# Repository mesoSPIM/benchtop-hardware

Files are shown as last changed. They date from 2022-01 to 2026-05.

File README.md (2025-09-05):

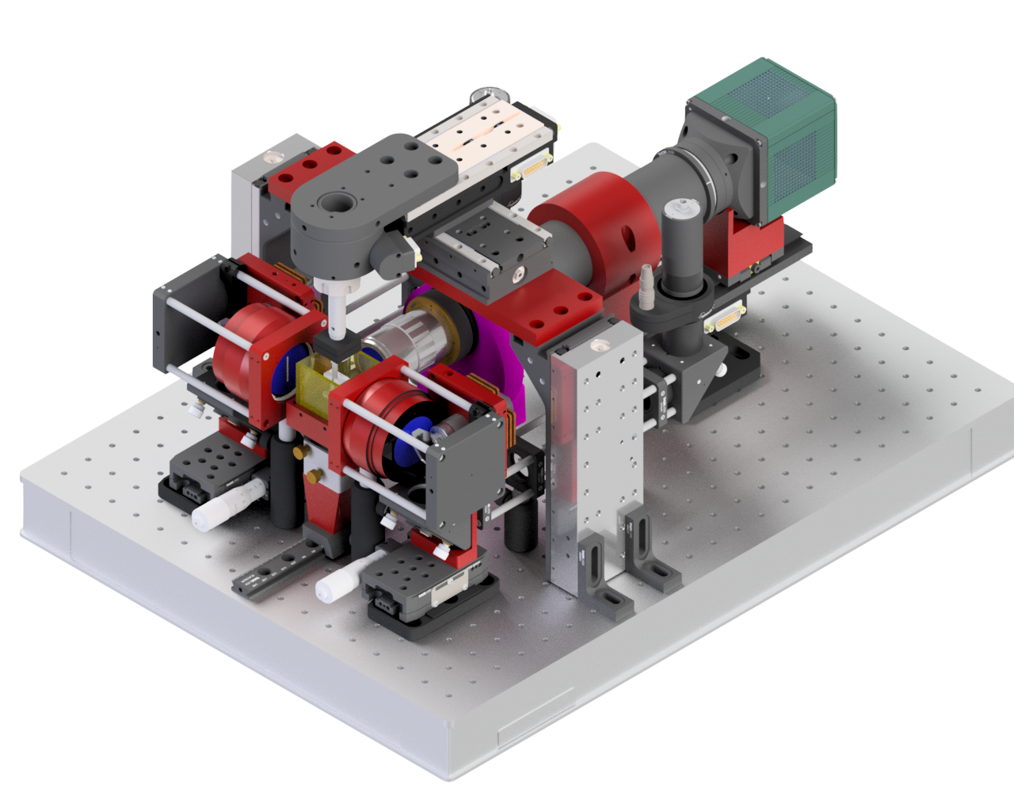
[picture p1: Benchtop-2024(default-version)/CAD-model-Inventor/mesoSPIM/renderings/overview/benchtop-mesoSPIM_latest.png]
Benchtop V2


# Benchtop mesoSPIM hardware documentation

## Who is the mesoSPIM project for?
* You are looking for a versatile imaging platform for cleared tissue that can be tailored to your needs.
* Research groups and imaging facilities with experience in building and supporting custom microscopes.

## What are ideal imaging applications for a mesoSPIM?
* screening of large numbers of cleared samples
* imaging of cell populations or other structures (blood vessels, plaques, denrites, even axons) in whole cleared organs.

## Why Benchtop mesoSPIM?
Being able to move the microscope from one lab to another, bring it to workshops, and send it to collaborators greatly increases its accessibility for biologists. Lab space is often a scarce asset, and having a compact microscope on the bench gives many advantages compared to bringing your samples to a large instrument in a dedicated room. 

## Key differences to mesoSPIM-v5
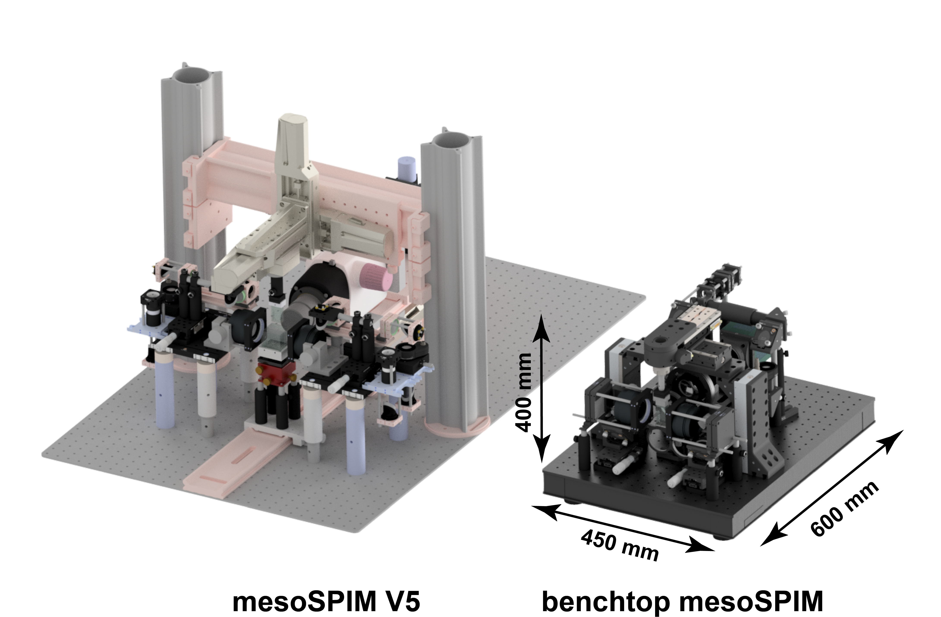
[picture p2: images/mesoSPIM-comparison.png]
mesoSPIM versions comparison


Benchtop mesoSPIM has smaller size, lower cost, higher image quality, and easier assembly than [previous version (V5)](https://github.com/mesoSPIM/mesoSPIM-hardware-documentation). 

| 					| **mesoSPIM v.5** | **Benchtop mesoSPIM** |
|----------|----------|--------------------|
|**Optical resolution, axial**| 5 $\mu m$ | 3.3 $\mu m$  | 
|**Optical resolution, lateral**| 2.7 $\mu m$ (at zoom 4x) | 2.0 $\mu m$ (1.5 - 2.6 $\mu m$ depending on the objective) | 
|**Magnification range**| 0.63x - 6.3x | 0.9x - 20x | 
| **Detection objectives** 	|  Variable magnification (via motorized zoom)  | Fixed-magnification (manual exchange) |
| **Camera sensor FOV (diagonal)** | 19 mm |  25 mm |
| **Pixel size** | 6.5 $\mu m$  | 4.25 $\mu m$  | 
| **Pixels/image** | 4 MP | 15 MP |
| **Footprint** | 1 $m^2$ |  0.25 $m^2$ |
| **Mobile** |  no | yes |
| **Approximate cost, EUR** | 162k | 95k | 

The cost estimate does not include PC workstation and a screen. V.5 costs include 4 laser lines (405, 488, 561, 638 nm) and optical table. Benchtop price includes the three most popular laser lines (488, 561, 638 nm) and 2x, 5x, 10x objectives. 

The number of custom parts in Benchtop is greatly reduced. 

The acquisition software remains the same, compatible with both versions of the microscope. 

## Build your own Benchtop
Our project is free and open-source, allowing anyone to build their own microscope. The [BT-mesoSPIM wiki](https://github.com/mesoSPIM/benchtop-hardware/wiki) will guide you how to build, setup, and use the BT-mesoSPIM system.

## Upgrade your existing v.4-5 mesoSPIM
(currently in beta) We also offer parts list and instructions for upgrading the detection optics of your existing mesoSPIM (v.4 and 5), so it can achieve the same resolution and image quality as the current Benchtop. See parts list and instructions for [mesoSPIM upgrade](https://github.com/mesoSPIM/benchtop-hardware/tree/main/v4-5-upgrade-2023).

# User guides
Introductory training of a new user typically takes 2 hours, ideally with a couple of follow-up sessions to make sure software parameters are set up correctly by the user. Our microscopy facility ZMB (Univerity of Zurich) has detailed guides on [mesoSPIM start-up, setting up, and acquisition](https://zmb.dozuki.com/c/Lightsheet_microscopy#Section_MesoSPIM).

## Citation
If you use any parts of this work for your project, please cite us:

Vladimirov, N., Voigt, F.F., Naert, T. et al. Benchtop mesoSPIM: a next-generation open-source light-sheet microscope for cleared samples. [Nat Commun 15, 2679 (2024).](https://doi.org/10.1038/s41467-024-46770-2)

## Discussion
Since August 2025 we joined the vibrant [image.cs forum](https://forum.image.sc/tag/mesospim)



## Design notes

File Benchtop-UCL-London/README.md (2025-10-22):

### UCL London version
This version of Benchtop mesoSPIM ([setup #29](https://mesospim.org/setups/)) was modified and shared by [Tchern Lenn](mailto:<y.lenn@ucl.ac.uk>) at the [UCL Cancer Institute Microscopy and Imaging Translational Technology Platform](https://www.ucl.ac.uk/cancer/research/cancer-institute-translational-technology-platforms/microscopy-and-imaging-translational). 

The advantages of this modification include:
- 6 laser lines
- alternative NI components for reduced cost

The key changes to the default setup:
- Filter wheel with 8 slots (ZWO EWF 8x31 mm).
- Elevation of the 3D printed detection path components to accomodate larger filter wheel
- NI signal generation card (PXIe-6738)
- NI Terminal block
- NI Card Chassis (PXIe-1090)
- Laser Combiner with 6 lasers

IMPORTANT NOTE!
The new chassis connects to the PC via a **thunderbolt** connection. No special card (eg. PCIe-8363) is needed but an available thunderbolt port on the PC is required.

## Files
Source files and parts list related to this version can be found above.

## Wiki
Wiki pages can be found [here](https://github.com/TchLenn/benchtop-hardware/wiki)

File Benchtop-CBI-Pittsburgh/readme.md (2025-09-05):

# Immersion chamber

- 3D printed using consumer-grade printer
- resistant to BABB, DBE, or other organic solvents
- low cost
- perfect alignment, no astigmatism
- robust against clumsy users
- thin walls, less spherical aberration
- large volume, fits large samples

# Documentation
[Mesospim cuvettes.pptx](./docs/Mesospim_cuvettes.pptx)


# Parts list
[Cuvette Parts List](./parts-list/parts-list-immersion-cuvette.xlsx)

## Credits
Designed at [CBI Pittsburgh](https://www.cbi.pitt.edu/) by Simon Watkins and Travis Wheeler.

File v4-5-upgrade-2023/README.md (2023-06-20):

*Currently in beta-testing!*

## Upgrade overview
Upgrading the detection objectives of your mesoSPIM can significantly boost your system resolution, while using newer cSMOS cameras (e.g. Teledyne Photometrics Iris 15 or Kinetix) can aditionally boost your throughput.

The suggested upgrade requires 5 Mitutoyo Plan Apo objectives (2x, 5x, 7.5x, 10x, 20x), a motorized turret, a compact filter wheel, mounting hardware, and, optionally, a large-sensor sCMOS camera (we recommend Teledyne Photometrics Iris 15).

SI-Fig-Detection-arm-upgrade

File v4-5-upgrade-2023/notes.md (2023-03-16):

## Ludl filter wheel
There are several problems with Ludl:
* they are bulky
* require custom adapters for Thorlabs SM2 lens tube
* over time the plastic belt can get torn
* require dedicated COM card and configuring COM port (which can change after Windows update)

## Zwo EFWmini filter wheel
Several advantages:
* small and low-cost (200$ vs 6k for Ludl)
* works from USB
* takes up filters up to 31 mm
* easy mechanical interface with T-mounts on each side, available from Thorlabs

### Detection arm optical axis height
From the upper rail carriage (Newport M-CXL95) to detection optical axis H=94 mm (v4,5)

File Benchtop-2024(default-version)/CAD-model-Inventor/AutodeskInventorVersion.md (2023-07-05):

# Autodesk Inventor version
The current version we are using is 2023. Unfortunately Autodesk keeps updating the version of our license, so there are some files that were created using 2017, 2019, or 2021 versions.

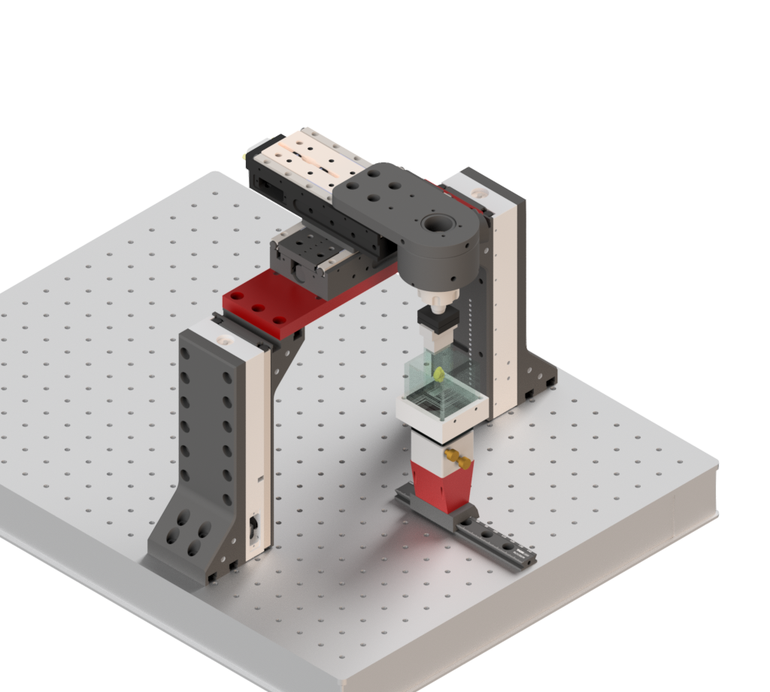
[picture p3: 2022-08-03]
Benchtop-2024(default-version)/CAD-model-Inventor/mesoSPIM/renderings/sample-stages-handling/stages-overview3.png

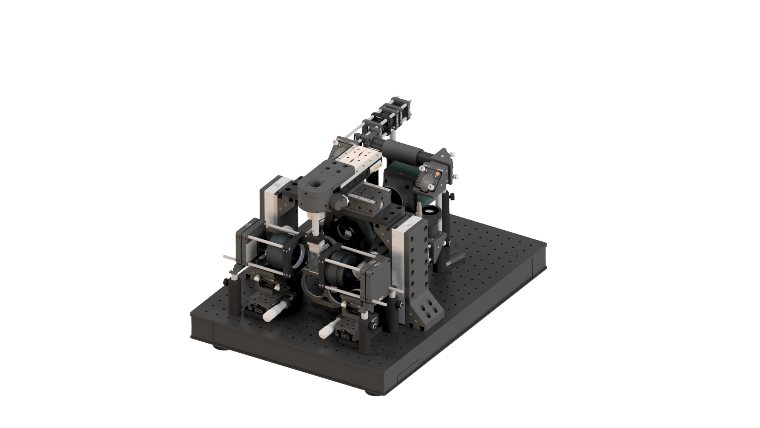
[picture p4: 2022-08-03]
Benchtop-2024(default-version)/CAD-model-Inventor/mesoSPIM/renderings/overview/view1/benchtop-mesoSPIM-V2-1-full.png

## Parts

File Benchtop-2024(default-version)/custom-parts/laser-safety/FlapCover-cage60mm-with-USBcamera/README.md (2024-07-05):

# Snap-on laser cover with integrated webcam mount for 60-mm Thorlabs cage system

# 3D printing
Extrusion printer (eg Prusa), PETG or similar material.

# Compatibe webcams
- `DFRobot FIT0701` (70-deg FOV)
- `HBVCAM-3M2111 V22` (110 deg FOV)

# Mounting hardware
- M3 screws 5 mm long screwed in directly into the holes.

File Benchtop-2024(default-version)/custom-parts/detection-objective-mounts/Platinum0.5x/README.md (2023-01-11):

## Warning
While it is possible to mount and use Edmund Platinum 0.5x telecentric lens with this mount, the galvo scanning range (for Thorlsbs 15-mm beam galvos) 
is too high to cover such large FOV at required frequency (100 Hz). As a result, the galvo flaps with weird noises.

So, use this lens at your own risk, possibly with smaller and lighter galvos, high-perfomance galvo driver, and watch for scanning issues.

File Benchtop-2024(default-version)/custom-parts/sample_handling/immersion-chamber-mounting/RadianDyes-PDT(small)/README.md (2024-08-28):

3D printed adapter for RadiantDyes RD-PDT-S (small) prism holder mounted on Thorlabs RC2 carier (dovetail rail).
- For cuvette height 45 mm, use `RD-PDT-S-to-RC2-height40mm.stl` model
- For cuvette height 75 mm, use `RD-PDT-S-to-M4-bolts-Base-H10mm.stl` model

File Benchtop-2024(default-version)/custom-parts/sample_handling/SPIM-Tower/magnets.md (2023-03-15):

Magnets size: D=2 mm, H=3-6 mm.

[Source in Switzerland](https://www.supermagnete.ch/stabmagnete-neodym-rund?length-or-diameter=2.00,2.00&height=3.00,3.00)

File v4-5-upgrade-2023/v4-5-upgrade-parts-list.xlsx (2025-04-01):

Part # | Vendor | Description | QTY | Unit Price (USD) | Price (USD) | Comment
Camera
01-IRIS-15-PCIe-M-16-C | Photometrics | IRIS-15-PCIe sCMOS camera | 1 | 12350.00 | 12350 | FOV 25 mm diagonal
Detection: Filter wheel
ZWO EFW 7x36mm | ZWO | ZWO EFW 7x36mm (https://astronomy-imaging-camera.com/product/new-zwo-efw-7x36mm/) | 1 | 299.00 | 299 | Check local distributors (astronomy shops). Alternative for small (25 mm) filters: 5-slot filter wheel for 25-mm filters
32mmFilterAdapter.stl | 3D printed (SLS) | Adapter to hold 32 mm filters in 36 mm slots | 5 | 10.00 | 50 | 32 mm filter in 36 mm slots (available 25mm filter for 31 mm slots). See /custom-parts/detection-accessories for printable 3D model
SM2T2 | Thorlabs | SM2 (2.035"-40) Coupler, External Threads, 1/2" Long | 1 | 37.00 | 37 | SM2 coupler to rotate the F mount (camera) relative to filter wheel
SM2V10 | Thorlabs | Ø2" Adjustable Lens Tube, 0.81" Travel | 1 | 54.00 | 54 | SM2 coupler to mount and rotate the turret relative to filter wheel
TMA4 | Thorlabs | Adapter with External T-Mount to Internal SM2 | 2 | 24.00 | 48 | Adapters for both sides of the ZWO EFW Mini filter, which has T-mount threads (M42)
Detection: objectives and revolver
5-slot motorized turret + 5 objectives
378-726D | Mitutoyo | Bright field motorized revolver | 1 | 4655.00 | 4655 | The turret for Mitutoyo Plan Apo objectives
12AAA807D | Mitutoyo | RS-232C cable 2 m | 1 | 75 | 75 | accessory
378-089 | Mitutoyo | Parfocal adjustment shim set | 1 | 136 | 136 | accessory
MotorizedRevolver-SM2-adapter | Mechanical shop | Adapter between motorized revolver and Thorlabs SM2 tube | 1 | 200 | 200 | Machined from Alu, requires SM2 threads
SM2L10 | Thorlabs | 1" long SM2 tube | 1 | 26.00 | 26 | Adapter: Motorized revolver to filter wheel. Replaced by SM2V10 to allow rotation.
378-801-12 | Mitutoyo | Objective M Plan APO 2X | 1 | 801 | 801
378-802-6 | Mitutoyo | Objective M Plan APO 5X | 1 | 718 | 718
378-807-3 | Mitutoyo | Objective M Plan APO 7.5X | 1 | 1391 | 1391
378-803-3 | Mitutoyo | Objective M Plan APO 10X | 1 | 883 | 883
378-847 | Mitutoyo | Mitutoyo G Plan APO 20X/t3,5 (https://shop.mitutoyo.ch/web/mitutoyo/en_CH/mitutoyo/05.04.02/G%20Plan%20APO%2020X-t3%2C5/PR/378-847/index.xhtml;jsessionid=CFD835C47751CA929FEA384183C0A21D) | 1 | 3670.00 | 3670
Detection: Tube lens and camera F-mount
36-401 | Edmund Optics | Mitutoyo MT-1 Accessory Tube Lens (https://www.edmundoptics.com/p/mt-1-accessory-tube-lens/11488/) | 1 | 752.00 | 752 | Preferred choice for Mititoyo objectives, except the 2X/0.055 one. Ordered from Edmund for historical reasons, update part number to Mitutoyo
Adapter-MitutoyoMT1-SM2-v3(flex).stl | 3D printed | Adapter for SM2 lens tube, attached to SM2 retaining ring | 1 | 50.00 | 50
SM2E60 | Thorlabs | SM2 Series Extension Tube, 6" | 1 | 65.00 | 65 | Tube lens is inserted inside this tube
SM2M20 | Thorlabs | SM2 Lens Tube Without External Threads, 2" Thread Depth | 1 | 32.00 | 32 | Extends the SM2E60 and mounts to the SM2NFM2
SM2NFM2 | Thorlabs | Adapter with External SM2 Threads and Male F-Mount Ring | 1 | 112.00 | 112 | Adapter to camera with F-mount
 |  |  |  | 584.00
Detection Assembly Mounting (on the X95 rail carriage)
ThorlabsSM2L30-XT66P2M_H94mm(axis2base) | 3D printed | Rail carriage mount of the SM2 tube assembly | 2 | 50 | 100 | Bolted to the Newport CXL95 rail carriages (M6 bolts)
XT95-500 | Thorlabs | 95 mm Construction Rail, Clear Anodized, L = 500 mm | 3 | 150 | 0 | Gantry elements, ONLY for mesoSPIM-v4 upgrade
XT95P3 | Thorlabs | Base Plate for 95 mm Rails | 2 | 53 | 0 | Gantry elements, ONLY for mesoSPIM-v4 upgrade
XT95RC4/M | Thorlabs | Drop-On Rail Carriage for 95 mm Rails, 100.0 mm Long, M6 Tapped Holes | 3 | 128 | 0 | Gantry elements, ONLY for mesoSPIM-v4 upgrade
XT95RC1/M | Thorlabs | Drop-On Rail Carriage for 95 mm Rails, 25.0 mm Long, M6 Tapped Holes | 2 | 77 | 0 | Gantry elements, ONLY for mesoSPIM-v4 upgrade
camera-dependent | camera-dependent | Camera-specific support structure | 1 | 50 | 50 | Photometrics Iris 15: ToDo. Orca Lightning: Breadboard 200 mm wide that supports the weight of the camera
 |  |  |  | Total, USD | 26554

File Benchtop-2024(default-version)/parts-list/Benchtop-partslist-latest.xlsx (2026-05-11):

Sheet: Main
DISCLAIMER: All prices are approximate and subject to change by the vendors without prior notice
Part # | Vendor | Description | QTY | Unit Price (USD) | Price (USD) | Assembly | Subassembly | Comment
Camera
01-IRIS-15-PCIe-M-16-C | Photometrics | IRIS-15-PCIe sCMOS camera | 1 | 15000 | 15000 | Detection arm |  | FOV 25 mm diagonal, programmable rolling shutter, 15MP sensor
Excitation laser combiner options
Recommended laser combiner specs: 3-4 lasers: (405 optional), 488, 561, 638 nm, power 50-150 mW. Digital and analog power modulation. Coupling to SM fiber with FC/APC end connector.
Currently recommended: | TOPTICA | CLE-50 combiner (405nm, 488nm, 561nm, 640nm: 50 mW each) | 2 | 29000 | 58000 | Excitation |  | Typically very stable and reliable lasers. For more budget lasers, CLE-20 or CLE-30 (20 and 30 mW per chanel) can be considered.
Legacy: | Oxxius | L4Cc 488-561-638 nm, 100 mW each, 2 fiber ports, switching module MDL-FSTM | 0 | 25000 | 0 | Excitation |  | Warning: Oxxius is a budget laser, with frequent quality issues. See overview at (https://github.com/mesoSPIM/benchtop-hardware/wiki/Laser-selection). Includes switching module between 2 laser ports, controlled by TTL signal. The 405nm is NOT included! A four-laser version is ~35k.
Sample & Microscope Stages
Dual-LS100-FTP-K0 | ASI | Two parallel LS-100 servo actuators, table mounting brackets not included | 0 | 6500 | 0 | Sample motion |  | Sample Y stage
LS-50-AMCCH | ASI | LS-50 Linear Stage, with sub-micron accuracy, and 50 mm of travel | 0 | 2250 | 0 | Sample motion |  | Sample X stage
LS-5012 | ASI | Plate for attaching flat surface of linear stage to breadboard. 3.9" x 5.9" | 0 | 160 | 0 | Detection arm | Detection path
LS-50-AMCLH | ASI | LS-50 Linear Stage, with sub-micron accuracy, and 50 mm of travel | 0 | 2250 | 0 | Detection arm | Detection path | Focus (F) stage, moves camera and detection lens assembly
DV-6010-C | ASI | Dovetail mount pair (VTS-2112 & CDZ-1010) 60 x 62 x 10 mm overall dimensions. | 0 | 230 | 0 | Sample motion |  | Cross-coupling X and Z stage adapter
LS-50S-AMECHS | ASI | LS-50 Linear Stage, with sub-micron accuracy, 50 mm of travel, and stainless steel slide | 0 | 2425 | 0 | Sample motion |  | Sample Z-stage
LE-LS-HH-70 | ASI | Encoder Linear LE Heidenhain 70mm scale installed on AMECHS stage | 0 | 3000 | 0 | Sample motion |  | Sample Z-stage encoder
C60-3060-CMR-1011 | ASI | LS-50 slide to C-mount adapter | 0 | 150 | 0 | Sample motion |  | Rotary stage adapter
C60-3060-SRS | ASI | Rotary stage with collet for holding a sample. | 0 | 3000 | 0 | Sample control |  | Sample Rotation (R) stage
STAGE-4D-MESOSPIM-K1 | ASI | All stage parts above offered by ASI (Jon Daniels <jon@asiimaging.com>) | 1 | 19965 | 19965 |  |  | Bundle of 6 stages with mounting hardware
TG8-BASIC | ASI | Controller: Includes TG8, TGCOM, 2x TGDCM2, SA-JOY+ZF Contols four DC servo motors, | 0 | 5800 | 0 | Motion control |  | Motion controller with pre-installed cards
TGDCM2-1RE | ASI | Dual Axis motion control card - one slot. Modified for 2nd axis always rotary encoded. | 0 | 1100 | 0 | Motion control |  | Motion controller card
TG8-MESOSPIM-K1 | ASI | The controller bundle offered by ASI | 1 | 6900 | 6900 |  |  | Bundle of motion controller
MESOS-11 or mesoSPIM-Bridge-wide | ASI or Mechanical shop | Bridge part between two parallel LS-100 servo actuators | 1 | 160 | 0 | Sample motion |  | Bridge for XZR stage assembly. NOT included in the STAGE-4D-MESOSPIM-K1 (above), but included in MESOS-MACH-K1 (below).
MESOS-MACH-K1 | ASI | kit of metal machined parts for benchtop mesoSPIM | 0 | 1740 | 1740 | Sample motion and Excitation |  | Kit includes MESOS-11, qty 14 MESOS-10, and qty 2 each MESOS-01, MESOS-12, and MESOS-13
AB90H | Thorlabs | Slim Right-Angle Bracket with Counterbored Slots | 5 | 27 | 135 | Sample motion |  | 4x: Table mounting for the Y axis (two parallel LS-100 servo actuators Dual-LS100-FTP); 1x: for galvo board heat sink mounting
Sample handling
KB25/M | Thorlabs | Complete 25 mm x 25 mm Kinematic Base, Top and Bottom Plates, M4 Counterbores | 2 | 70 | 140 | Sample handling |  | Magnetic bases to attach sample holders and immersion cuvette
KBB25/M | Thorlabs | Bottom Plate Only of the KB25/M Kinematic Base, M4 Counterbore | 6 | 36 | 216 | Sample handling |  | Sample holder side (nests, not balls) of the kinematic base
TR50/M | Thorlabs | Ø12.7 mm Optical Post, SS, M4 Setscrew, M6 Tap, L = 50 mm | 1 | 6 | 6 | Sample handling |  | Connection of theta-stage chuck to the sample holder.
PH50/M | Thorlabs | Ø12.7 mm Post Holder, Spring-Loaded Hex-Locking Thumbscrew, L=50 mm | 1 | 9 | 9 | Sample handling |  | Connection of theta-stage chuck to the sample holder. Use M6 bolt in the chuck to connect
RLA150/M | Thorlabs | Dovetail Optical Rail, 150 mm, Metric | 1 | 43 | 43 | Sample handling |  | Immersion cuvette base
RC2/M | Thorlabs | Dovetail Rail Carrier, 50.8 mm x 25.4 mm, M6 Counterbore, M4 Taps | 1 | 29 | 29 | Sample handling |  | Rail carrier for immersion cuvette base
RD-PDT-S | Radiant Dyes | Prism Turn Table Small | 1 | 195 | 195 | Sample handling |  | Base for immersion cuvette
RD-PDT-S-to-M4-bolts-Base-H10mm | 3D printed | Adapter for mounting RD-PDT-S to Thorlabs rail carrier RC2, cuvettes 75 mm tall | 1 | 10 | 10 |  |  | See file RD-PDT-S-to-M4-bolts-Base-H10mm.ipt (.stl) for details.
Computer
The following specs are suggested for acquisition, not for storage, visualization or image processing
CPU | Intel Xeon W-2145, W-2245 or Intel Core i9-9900K, or newer, high-performance for single-threaded applications
RAM | 128 GB DDR4
OS drive | 1 TB SSD NVMe
Fast storage (for streaming) | 2 TB or more SSD NVMe drive
IO | one PCIe x1 (or higher) and one PCIe x4 (or higher) slot.
OS | Windows 11 Pro LTSC
Monitor | 30 inch
Excitation arms
PBG52522 | Thorlabs | UltraLight Series II Breadboard, 450 x 600 x 55 mm, M6 Taps | 1 | 728 | 728 | Base |  | Microscope base
AV4/M | Thorlabs | Ø45.0 mm Sorbothane Feet, Internal M6 Mounting Thread, 4 Pieces | 1 | 33 | 33 | Base |  | Attached to the bottom of the PBG52522 Breadboard. Based on Benchtop weight 25 kg on breadboard (including BB).
SM1FCA | Thorlabs | FC/APC Fiber Adapter Plate with External SM1 (1.035"-40) Threads, Wide Key (2.2 mm) | 2 | 31 | 62 | Excitation | Laser collimator | Oxxius ships with PM-S405-XP+ optical fiber, NA=0.11.
AC254-060-A-ML | Thorlabs | f=60 mm, Ø1" Achromatic Doublet, SM1-Threaded Mount, ARC: 400-700 nm | 2 | 99 | 198 | Excitation | Laser collimator | Recommended achromat, depends of optical fiber NA, see https://github.com/mesoSPIM/benchtop-hardware/wiki/Excitation-arms-assembly
SM1M20 | Thorlabs | SM1 Lens Tube Without External Threads, 2" Long, Two Retaining Rings Included | 2 | 17 | 34 | Excitation | Laser collimator | This tube is minimal , for f=50 mm achromat. It must be extended by 0.3", 0.5" or 1" tubes for f=60, 70, or 75 mm achromats.
SM1L03 | Thorlabs | SM1 Lens Tube, 0.30" Thread Depth | 2 | 12 | 24 | Excitation | Laser collimator | Tube extension for f=60 mm achromat
SM1L05 | Thorlabs | SM1 Lens Tube, 0.50" Thread Depth | 2 | 12 | 24 | Excitation | Laser collimator | Tube extension for f=70 mm achromat
SM1L10 | Thorlabs | SM1 Lens Tube, 1" Thread Depth | 2 | 14 | 28 | Excitation | Laser collimator | Tube extension for f=75 mm achromat
SM1A10 | Thorlabs | Adapter with External SM1 Threads and Internal C-Mount Threads | 2 | 18.4127496 | 36.8254992 | Excitation | Adapter
33-494 | Edmund Optics | Optotune EL-16-40-TC-VIS-5D-C lenses | 2 | 935 | 1870 | Excitation | ETL Unit
88-940 | Edmund Optics | Optotune Lens Driver EL-E-4i | 2 | 365 | 730 | Excitation | ETL Unit | Modified: BNC cables need to be soldered: see https://github.com/mesoSPIM/mesoSPIM-hardware-documentation/wiki/mesoSPIM_preparing_ETL_drivers
varies | Digitec or elsewhere | Powered USB-Hub, eg Icy Box IB-HUB1405 | 1 | 40 | 40 | Excitation | ETL Unit | Simple USB-Hub for powering the ETL-Drivers
88-941 | Edmund Optics | Optotune 6-way Hirose Male/Female Cable, 1m Length | 2 | 90 | 180 | Excitation | ETL Unit
SM1A9 | Thorlabs | Adapter with External C-Mount Threads and Internal SM1 Threads, 4.4 mm Spacer | 2 | 18 | 36 | Excitation | Adapter
SM1T2 | Thorlabs | SM1 (1.035"-40) Coupler, External Threads, 0.5" Long | 2 | 21.21 | 42.42 | Excitation | Adapter | Distance adjustment
SM1L10 | Thorlabs | SM1 Lens Tube, 1.00" Thread Depth, One Retaining Ring Included | 2 | 13 | 26 | Excitation | Adapter
KCB1E/M | Thorlabs | Right-Angle Kinematic Elliptical Mirror Mount with Tapped Cage Rod Holes, 30 mm Cage System and SM1 Compatible, M4 and M6 Mounting Holes | 4 | 189 | 756 | Excitation | Laser folding | M1, M2 fold mirrors, in each arm
BBE1-E02 | Thorlabs | 1" Broadband Dielectric Elliptical Mirror, 400 - 750 nm | 4 | 110 | 440 | Excitation | Laser folding | M1, M2 fold mirrors, in each arm
CP33/M | Thorlabs | SM1-Threaded 30 mm Cage Plate, 0.35" Thick, 2 Retaining Rings, M4 Tap | 8 | 16 | 128 | Excitation | Cage assembly | 4 per arm
AC254-100-A-ML | Thorlabs | f=100 mm, Ø1" Achromatic Doublet, SM1-Threaded Mount, ARC: 400-700 nm | 4 | 104 | 416 | Excitation | The 1:1 relay from ETL to galvo | Lenses L2, L3 in the design view
ER8-P4 | Thorlabs | Cage Assembly Rod, 8" Long, Ø6 mm, 4 Pack | 2 | 41 | 82 | Excitation | The 1:1 relay from ETL to galvo | 4 rods per arm
ER12 | Thorlabs | Cage Assembly Rod, 12" Long, Ø6 mm | 2 | 17 | 34 | Excitation | Excitation obj mount | Rods that hold the excitation objectives in 60-mm cage
ER4 | Thorlabs | Cage Assembly Rod, 4" Long, Ø6 mm | 4 | 7 | 28 | Excitation | Excitation obj mount | Rods that hold the excitation objectives in 60-mm cage
ER1 | Thorlabs | Cage Assembly Rod, 1" Long, Ø6 mm | 4 | 5 | 20 | Excitation | Excitation obj mount | Rods that hold the excitation objectives in 60-mm cage
91863 | Nikon | Nikon AF-S 50 mm f/1.4 G Objective | 2 | 400 | 800 | Excitation | Excitation obj | Modified manually
MESOS-01 or LCP31M-Nikon-modified | ASI or Mechanical workshop | Nikon objective mount using Thorlabs LCP31/M 60 mm Blank Cage Plate | 2 | 300 | 600 | Excitation | Excitation obj mount | The part is offered by ASI as "MESOS-01 - CAGE ADAPTER". If DIY, see /custom-parts/excitation-objective/LCP06M-Nikon-modified.ipt
LCP31/M | Thorlabs | 60 mm Blank Cage Plate, M4 Tap (supersedes obsolete LCP03) | 0 | 36 | 0 | Excitation | Excitation obj mount | If DIY, lathe turning or similar machining is required, see /custom-parts/excitation-objective/
SM2NFMA or (discontinued) SM2NFM | Thorlabs | Adapter with External SM2 Threads and Nikon Female F-Mount Ring | 2 | 92 | 184 | Excitation | Excitation obj mount | Goes into LCP06M-Nikon-modified. If DIY, the F-mount steel ring must be taken out and mounted into the modified LCP06M plate using screws.
Cage60mm-2sides-InnerD75mm-L75mm | 3D printed | Laser safety snap-on covers | 2 | 1 | 2 | Excitation | Excitation obj mount | See the STL file in folder /custom-parts/laser-safety/Universal-cage60mm-L75mm(Benchtop)
PH50/M | Thorlabs | Ø12.7 mm Post Holder, Spring-Loaded Hex-Locking Thumbscrew, L=50 mm | 4 | 7 | 28 | Excitation | The 1:1 relay from ETL to galvo | Optical cage support, 2 per arm
TR40/M | Thorlabs | Ø12.7 mm Optical Post, SS, M4 Setscrew, M6 Tap, L = 40 mm | 4 | 5 | 20 | Excitation | The 1:1 relay from ETL to galvo | Optical cage support, 2 per arm
UPH50/M | Thorlabs | Ø12.7 mm Universal Post Holder, Spring-Loaded Locking Thumbscrew, L = 50 mm | 2 | 35 | 70 | Excitation | Excitation obj mount, compatible with 3D printed immersion chambers.
TR75/M | Thorlabs | Ø12.7 mm Optical Post, SS, M4 Setscrew, M6 Tap, L = 75 mm | 2 | 5 | 10 | Excitation | Excitation obj mount, compatible with 3D printed immersion chambers.
XRN25P/M | Thorlabs | Compact 25 mm Travel Linear Translation Stage, Side Micrometer, 1/4"-20 Taps | 2 | 398 | 796 | Excitation | M3 mirror assembly | Linear stage for M2 mirror adjustment. Right-arm stage must be converted, so the adjustment screw is put on the left side of the stage. See Micrometer Conversio tab at https://www.thorlabs.com/newgrouppage9.cfm?objectgroup_id=11015
MESOS12 or mirror-bracket.ipt | ASI or Mechanical workshop | Braket for M3 kinematic mirror mount | 2 | 150 | 0 | Excitation | M3 mirror assembly | The part is offered by ASI as "MESOS-12". Bracket for M2 mirror mounting on linear stage. Folder /custom-parts/excitation-mirror-bracket/
XRN-B1/M | Thorlabs | Base Plate for Stages with 2" Dovetails, Metric Slot Spacing | 2 | 30 | 60 | Excitation | M3 mirror assembly | Adapter plate for linear stage
MESOS13 or QS15-mount-modified-Thorlabs-LCP31 | ASI or Mechanical workshop | Modified 60 mm Blank Cage Plate | 2 | 300 | 0 | Excitation | Galvo assembly | The part is offered by ASI as "MESOS-13 GALVO MOUNT" in the bundle. If DIY, see files in /custom-parts/galvo-assembly/15mm-galvo(Thorlabs-QS15)-mount/
LCP31/M | Thorlabs | 60 mm Blank Cage Plate, M4 Tap (supersedes obsolete LCP03) | 0 | 36 | 0 | Excitation | Galvo assembly | Stock material for the galvo mount. Included in ASI bundle. If DIY, needs modification (machining), see /custom-parts/galvo-assembly/15mm-galvo(Thorlabs-QS15)-mount/
LCP33B | Thorlabs | 60 mm Cage Mounting Bracket | 2 | 32 | 64 | Excitation | Galvo assembly | Bracket to attach the galvo mount to the 60 mm cage
LCP31/M | Thorlabs | 60 mm Blank Cage Plate, M4 Tap | 2 | 36 | 72 | Excitation | Galvo assembly | Side covers of the galvo assembly
QS15X-AG | Thorlabs | Ø15 mm Beam Galvo System, X-Axis Protected Silver Mirror | 2 | 2104 | 4208 | Excitation | Galvo assembly | Standard cables are 60 cm long.
CBLS3F | Thorlabs | Command and Power Cables for QS15/20/30/45, SS, & SP Series Galvo Scanners | 2 | 82 | 164 | Excitation | Galvo assembly | Use your country code for correct plug and voltage.
GPS011-EC/US/JP | Thorlabs | 1D or 2D Galvo System Linear Power Supply, 110, 230, or 100 VAC (EC, US, JP option) | 1 | 520 | 520 | Excitation | Galvo assembly | Preferred power supply for 2 galvos. Needs a simple adapter (3 wires), see Wiki.
CBLS3P | Thorlabs | CBLS3P - Command and Power Cables for QS15/20 Scanning Galvanometer Systems and GPS011 Series Power Supply | 2 | 148 | 296 | Excitation | Galvo assembly | Kit cables with correct connectors for the GPS011 power supply
MESOS-10 or HeatSink-sheet-H2mm | ASI or Mechanical workshop | Galvo heat sink assembled from sheets, each galvo requires 7 sheets | 14 | 20 | 0 | Excitation | Galvo assembly | The part is offered by ASI as "MESOS-10". Can be laser-cut or water-jet cut from 2-mm Aluminum. See folder /custom-parts/galvo-assembly/15mm-galvo(Thorlabs-QS15)-mount/
QDM2 | Thorlabs | Heatsink and Mount for QG4, QG5, QS15, QS20, QS30, and QS45 Galvanometer System Servo Drivers | 2 | 181 | 362 | Excitation | Galvo assembly | For DIY heat sink, see /galvo-assembly/heatsink-servo-boards
AB90H | Thorlabs | Slim Right-Angle Bracket with Counterbored Slots. For mounting the heat sink to base breadboard. | 0 | 28 | 0 | Excitation | Galvo assembly | already accounted for, see AB90H, 5x, above
Detection: Camera and lens mount
LS-50-AMCLH | ASI | LS-50 Linear Stage, with sub-micron accuracy, and 50 mm of travel | 1 |  |  |  |  | see Sample and Microscopy Stages
XT66SD-250 | Thorlabs | 6 mm Single Dovetail Rail with Mounting Counterbores, L = 250 mm | 1 | 63 | 63
XT66P2/M | Thorlabs | Rail Carriage for 66 mm Rails with M4 & M6 Taps | 2 | 69 | 138
LS-5012 | ASI | Plate for attaching flat surface of linear stage to breadboard. 3.9" x 5.9" | 1 |  |  |  |  | see Sample and Microscopy Stages
Iris15-XT66P2M | 3D printed | Support for Iris15 camera, because F-mount does not hold the amera weight well. | 5 | 1 | 5 |  |  | Can be printed with a hobby printer, using eg PETG filament. See /custom-parts/detection-objective-mounts/
Detection: Filter wheel
5-slot filter wheel for 25-mm filters
ZWO EFW-MINI | ZWO | ZWO EFW Mini 5 x 31 mm (https://astronomy-imaging-camera.com/product/efw-mini) | 1 | 200 | 200 |  |  | Check local distributors (astronomy shops)
25mmFilterAdapter.stl | 3D printed (SLS) | Adapter to hold 25 mm filters in 31 mm slots | 5 | 1 | 5 |  |  | See /custom-parts/detection-accessories for printable 3D model
SM2L05 | Thorlabs | 0.5" long SM2 lens tube | 1 | 26 | 26 |  |  | Adapter: Objective to filter wheel, via M2M40S thread adapter
SM2T2 | Thorlabs | SM2 (2.035"-40) Coupler, External Threads, 1/2" Long | 1 | 37 | 37 |  |  | SM2 coupler to rotate the filter wheel and fix it at desired angle the with retaining ring
TMA4 | Thorlabs | Adapter with External T-Mount to Internal SM2 | 2 | 24 | 48 |  |  | Adapters for both sides of the ZWO EFW Mini filter, which has T-mount threads (M42)
Filters
Filters have to be selected according to lasers & needs (flurescent markers and dyes used). The single quadband is a MINIMALIST choice
F57-405 | Chroma (distributors: AHF in Germany, or europe@chroma.com in the rest of EU) | QuadLine Emission ZET405/488/561/640m, in 25 mm diameter | 1 | 625 | 625 | Detection path |  | A frequently used quad-band filter, allows all fluorescence through
Detection: Objectives
59-875 | Edmund Optics | Mitutoyo M Plan Apo, 2X/0.055 (https://www.edmundoptics.com/p/2x-eo-m-plan-apo-long-working-distance-infinity-corrected/16533/) | 1 | 900 | 900 | Detection path |  | Works better with Olympus SWTLU-C tube lens. Thread M26 x 36TPI
59-876 | Edmund Optics | Mitutoyo M Plan Apo, 5X/0.14 (https://www.edmundoptics.com/p/5x-eo-m-plan-apo-long-working-distance-infinity-corrected/16534/) | 1 | 767 | 767 | Detection path |  | Works best with the Mitutoyo MT-1 tube lens. Thread M26 x 36TPI
66-383 | Edmund Optics | Mitutoyo M Plan Apo 7.5X/0.21 (https://www.edmundoptics.com/p/75x-mitutoyo-plan-apo-infinity-corrected-long-wd-objective/20898/) | 0 | 1540 | 0 | Detection path |  | Works best with the Mitutoyo MT-1 tube lens. Thread M26 x 36TPI
59-877 | Edmund Optics | Mitutoyo M Plan Apo 10x/0.28 (https://www.edmundoptics.com/p/10x-eo-m-plan-apo-long-working-distance-infinity-corrected/16535/) | 1 | 877 | 877 | Detection path |  | Works best with the Mitutoyo MT-1 tube lens. Thread M26 x 36TPI
58-175 | Edmund Optics | Mitutoyo G Plan APO 20X/t3,5 (https://www.edmundoptics.com/f/mitutoyo-glass-thickness-compensated-infinity-corrected-objectives/14732/) | 0 | 4700 | 0 | Detection path |  | Corrected for 3.5 mm of glass (n1.52). Thread M26 x 36TPI.
SM1A27 | Thorlabs | Adapter with External SM1 Threads and Internal M26 x 0.706 (36 TPI) Threads | 1 | 20 | 20 | Detection path |  | Adapter from objective to ZWO filter wheel, part 1
SM2A6 | Thorlabs | Adapter with External SM2 Threads and Internal SM1 Threads | 1 | 25 | 25 | Detection path |  | Adapter from objective to ZWO filter wheel, part 2
Detection: Tube lens
54-774 | Edmund Optics | Mitutoyo MT-1 Accessory Tube Lens (https://www.edmundoptics.com/p/mt-1-accessory-tube-lens/11488/) | 1 | 752 | 752 | Detection path |  | Preferred choice for Mititoyo objectives, except the 2X/0.055 one
Adapter-MitutoyoMT1-SM2.stl | 3D printed | Adapter for SM2 lens tube, attached to SM2 retaining ring | 5 | 1 | 5 | Detection path |  | Not ideal (requires gluing it to SM2 ring), would be better to have all metal (cutom) part. TODO.
SM2E60 | Thorlabs | SM2 Series Extension Tube, 6" | 1 | 65 | 65 | Detection path |  | Tube lens is inserted inside this tube
SM2M20 | Thorlabs | SM2 Lens Tube Without External Threads, 2" Thread Depth | 1 | 32 | 32 | Detection path |  | Extends the SM2E60 and mounts to the SM2NFM2
SM2NFM2 | Thorlabs | Adapter with External SM2 Threads and Male F-Mount Ring | 1 | 112 | 112 | Detection path |  | Adapter to camera with F-mount
ThorlabsSM2L30-XT66P2M-BASE, -UPPER | 3D printed | 2-piece adapter (-BAS, -UPPER) for holding SM2 tubes | 5 | 2 | 10 | Detection path |  | Can be printed with a hobby printer, using eg PETG filament. See /custom-parts/detection-objective-mounts/
Electronics / Signal generation
778512-01 | National Instruments | NI PXI-6733 with 8 16-Bit Waveform Analog Outputs | 1 | 5420 | 5420 | Signal generation |  | The signal generation card, 8 analog and 8 digital channels. Potentially replaceable with two NI-PCIe-6323 cards (and no chassis), but this needs testing and possibly software changes.
781163-01 | National Instruments | NI PXIe-1073 Integrated MXIe, 5 Periph Slots | 1 | 2560 | 2560 | Signal generation |  | Chassis to mount the signal generation card. Alternative: low-cost NI PXI-1033 from second-hand market.
788814-01 | National Instruments | NI PCIe-8363, 1 Port MXI-Express Interface | 1 | 900 | 900 | Signal generation |  | Connects the Chassis to the PC. Alternative: a two-port PCIe-8362, or a discontinued PCIe-8361.
779500-03 | National Instruments | MXI-Express Cable, Gen 1 x1, Copper, 3m | 1 | 163 | 163 | Signal generation |  | Cable between the Chassis and the PC
763065-01 | National Instruments | Power Cord, 220V, 10A (plug country-specific) | 1 | 11 | 11 | Signal generation
777643-01 | National Instruments | BNC-2110 Noise Rejecting, Shielded BNC Connector Block | 1 | 520 | 520 | Signal generation
199006-01 | National Instruments | SH68-68-EPM Shielded Cable, 68 D-Type to 68 D-Type, 1M | 1 | 193 | 193 | Signal generation |  | The cable MUST be "-EPM". Other similarly looking cables with marking "-RDIO" are NOT suitable.
PAA236R | Thorlabs | SMB Coaxial Cable, 90° SMB Female to BNC Male, 36" (914 mm) | 10 | 12 | 120 | Signal generation |  | Depending on the laser control interface (Oxxius: SMB).
CA2806 | Thorlabs | SMA Coaxial Cable, SMA Male to BNC Male, 6" (152 mm) | 1 | 14 | 14 | Signal generation |  | Depends on laser interface. Oxxius: IO connector must be modified, pin24 (MDL-FSTM) and pin16 (GND Digital), to accept arm switching signal.
2249-C-12 | Thorlabs | 0.3 m BNC Cable | 5 | 15.25 | 76.25 | Signal generation
2249-C-24 | Thorlabs | 0.6 m BNC Cable | 10 | 16.5 | 165 | Signal generation
2249-C-60 | Thorlabs | 1.5 m BNC cable | 10 | 24 | 240 | Signal generation
2249-C-120 | Thorlabs | 3m BNC cable | 6 | 24 | 144 | Signal generation
T3285 | Thorlabs | BNC Adapter, T, Female-Male-Female (F-M-F) | 1 | 11 | 11 | Signal generation |  | Splitting the BNC trigger between Z- and F-cards of ASI controller.
General lab and optics supplies
CA6-EU | Thorlabs | European Union Compliant Duster w/ Integrated Nozzle, 400 mL | 2 | 25 | 50
MC-50E | Thorlabs | Lens Tissues, 25 Sheets per Booklet, 50 Booklets in a Closeable Box | 1 | 85.1 | 85.1
BKF12 | Thorlabs | Black Aluminium Foil | 2 | 32 | 64 |  |  | Sometimes useful
T743-2.0 | Thorlabs | High-Performance Black Masking Tape, 2" x 180' (50 mm x 55 m) Roll | 2 | 51.58 | 103.16
PSS7 | Thorlabs | 7-Piece Precision Screwdriver Set | 1 | 60 | 60 |  |  | Or other, cheaper sets
HW-KIT6 | Thorlabs | Imperial Screw Thread Adapter Kit | 1 | 136.48 | 136.48
HW-KIT6/M | Thorlabs | Metric Screw Thread Adapter Kit | 1 | 136.48 | 136.48
HW-KIT1/M | Thorlabs | M4 Cap Screw and Hardware Kit | 1 | 60.95 | 60.95
HW-KIT3/M | Thorlabs | M4 Setscrew and Hardware Kit | 1 | 119.416 | 119.416
HW-KIT4/M | Thorlabs | M6 Setscrew and Hardware Kit | 1 | 105.8 | 105.8
HW-KIT2/M | Thorlabs | M6 Cap Screw and Hardware Kit | 2 | 119.6 | 239.2
HW-KIT5 | Thorlabs | 4-40 Cap Screw and Hardware Kit | 1 | 100 | 100
TC3/M | Thorlabs | 15-Piece Balldriver and Hex Key Kit with Stand, Metric | 2 | 92 | 184
TC2 | Thorlabs | 20-Piece Balldriver and Hex Key Kit with Stand, Imperial | 1 | 96.23 | 96.23
SPW801 | Thorlabs | Adjustable Spanner Wrench | 1 | 102.44 | 102.44
SPW602 | Thorlabs | SM1 Spanner Wrench, Graduated, Length = 3.88" | 2 | 28 | 56
SI254 | Thorlabs | Shearing Interferometer with a 10-25.4 mm Beam Diameter Shear Plate | 1 | 490 | 490 |  |  | Interferometer for beam collimation
SICP | Thorlabs | 30 mm Cage System Adapter for Shearing Interferometers with Diffuser Viewing Screen | 1 | 77 | 77 |  |  | accessory
SM1T2 | Thorlabs | SM1 (1.035"-40) Coupler, External Threads, 0.5" Long, Two Locking Rings | 1 | 20 | 20 |  |  | accessory
CCM1-G01/M | Thorlabs | 30 mm Cage Cube-Mounted Protected Aluminum Turning Mirror, M4 Tap | 1 | 177 | 177 |  |  | accessory
CPA1 | Thorlabs | 30 mm Cage Alignment Plate with Ø0.9 mm Hole | 2 | 13 | 26 |  |  | Beam alignment
LCPA1 | Thorlabs | 60 mm Cage Alignment Plate with Ø1 mm Hole | 2 | 19 | 38 |  |  | Beam alignment
LCPA2 | Thorlabs | 60 mm Cage Fluorescent Alignment Plate, Ø1 mm Hole, Orange | 1 | 12 | 12 |  |  | Beam alignment
DG10-1500-H1-MD | Thorlabs | Ø1" SM1-Mounted Frosted Glass Alignment Disk w/Ø1 mm Hole | 2 | 35 | 70 |  |  | Beam alignment
TR200/M | Thorlabs | Ø12.7 mm Optical Post, SS, M4 Setscrew, M6 Tap, L = 200 mm | 2 | 9 | 18 |  |  | Excitation cage alignment jig, see details at https://github.com/mesoSPIM/benchtop-hardware/wiki/Excitation_alignment
TBS1000C | Tektronix | 2 Channel Digital Storage Oscilloscope | 0 | 520 | 0 |  |  | Basic 2-ch oscilloscope for signal troubleshooting. Optional.
 |  | Multiport-power outlets | 4
 |  | Cable wraps | 1 |  |  |  |  | Lots of them
 |  | Isopropanol p.a. for lens cleaning | 1
Sample cuvettes | Material: glass, RI=1.52. For quartz (e.g. CLARITY imaging, RI=1.47), replace UG with UQ in the part name.
 | 3D printer or mechanical workshop | Large-cuvette-mount-40mm-V3.ipt | 4 | 40 | 160 | Immersion chamber mount | Machined from POM (Polyoxymethylen) or 3D printed from PA12 (polyamide, nylon) | One for each planned immersion cuvette mount / imaging medium
 | Portmann Instruments | UG-753-H75 40x40x75 fire-fused | 2 | 515 | 1030 | Immersion chamber
 | Portmann Instruments | UG-203 5x10x45 | 4 | 25 | 100 | Immersion chamber
 | Portmann Instruments | UG-204 10x10x45 | 4 | 28 | 112 | Immersion chamber
 | Portmann Instruments | UG-205 10x20x45 | 6 | 121.5 | 729 | Immersion chamber
 |  |  |  | Total: | 136647.7515 | USD
Machined parts
Part name | Qty | Notes
HeatSink-sheet-H2mm (from 2mm Alu sheet) | 14 | made from 2mm Alu sheets: laser cutter, waterjet, or EDM
LCP06M-Nikon-modified | 2 | machined from Thorlabs LCP06M
mirror-bracket | 2 | machined from stock Alu
QS15-mount-modified-Thorlabs-CagePlate-LCP03 | 2 | machined from Thorlabs LCP03
3D printed parts from PETG (low-cost extrusion printers)
Part name | Qty | Notes
Cage60mm-2sides-InnerD75mm-L75mm | 2 | Laser safety snap-on cover
Mitutoyo-BD-black-ring.ipt | 5 | Only for Mitutoyo BD objectives
Adapter-MitutoyoMT1-SM2.stl | 1 | If Mututoyo MT-1 tube lens is used
Iris15-XT66P2M | 1 | For Iris15 camera support
ThorlabsSM2L30-XT66P2M-BASE, -UPPER | 1 | A 2-piece mount for SM2 tubes
RD-PDT-S-to-M4-bolts-Base-H10mm | 1 | Mounting adapter for RadiantDyes prism, for using 75-mm tall immersion cuvettes
3D printed parts from PA12 (SLS printer)
Part name | Qty | Notes
25mmFilterAdapter.stl | 5 | Can be also printed on hobby printer from PETG, but dimensions may be off
Large-cuvette-mount-40mm-V3.ipt | 3 | Can be machined from POM as well
sample/cuvette holders | varies | BABB/DBE resistant, autoclavable
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

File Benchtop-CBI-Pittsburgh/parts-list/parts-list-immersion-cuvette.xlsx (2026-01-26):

Part # | Vendor | Name | QTY | Unit Price (USD) | Price (USD) | Comment | URL1 | URL2
Original Version (CBI Pittsburgh): glass windows 38 mm wide
cuvette-v1.STL | self-printed | Cuvette frame | 5 | 20 | 100 | Can be printed using Formlabs4 printer, suing Clear V5 Resin, with curing. CAD models in "...\custom_parts\ImmersionChambers\"
varies | Amazon or AliExpress | ULANZI Claw Quick Release Base Mount Upgraded Version | 5 | 20 | 100 | Base mount to breadboard + cuvette plate (kit) | https://de.aliexpress.com/item/1005007537889780.html
varies | Amazon or AliExpress | Ulanzi U-100 Ball Head for Tripod With Claw Quick Release Plate Mount | 1 | 30 | 30 | Ulanzi U-100 Ball Head for Tripod With Claw Quick Release Plate Mount | https://de.aliexpress.com/item/1005001758039535.html
3875-plus | Brain Research Laboratories | 38 x 75 x 1.0mm Adhesion Superfrost Plus (1 gross/144 slides) | 1 | 164 | 164 | Original slides used in CBI Pittsburgh | https://brainresearchlab.com/product/adhesion-superfrost-plus-microscope-slides/
66239195 | varies | Red Devil Sealant: 10.1 oz Cartridge, Clear, Silicone | 1 | 15 | 15 | Any similar consumer-grade silicone should do, but some are too viscous and hard to apply | https://www.mscdirect.com/product/details/66239195
Presentation: docs/Mesospim_cuvettes.pptx
Modification (UZH): glass windows 50 mm wide
cuvette-w70mm-slide50x75mm-v2.stp | SLS printed from PA12 | cuvette frame, inner dimensions: 65x55x80mm | 5 | 50 | 250 | Larger cuvette than the original. CAD models in "...\custom_parts\ImmersionChambers\Slide-50x75mm-v1"
varies | Amazon or AliExpress | ULANZI Claw Quick Release Base Mount Upgraded Version | 5 | 20 | 100 | same as in the original
249-75X50 | Corning | Microscope slides plain pre-cleaned 75x50x1 mm | 1 | 415 | 415 | Modification (wide slides). Actual slide width is 51 mm, not 50. Come in huge box of 720 slides. | https://ecatalog.corning.com/life-sciences/b2b/CH/en/General-Labware/Slides/Corning%C2%AE-Plain-Microscope-Slide/p/2947-75X50 | https://www.fishersci.com/shop/products/plain-microscope-slides-15/125535B
SI595 | Henkel | Loctite SI 595 | 1 | 25 | 25 | Medium viscous, can be squezed out with moderate force. Alternative to Red Devil, avaliable in Europe. | https://www.henkel-adhesives.com/pa/en/product/flexible-sealants/loctite_si_595.html
UBP2/M | Tholabs | Universal Base Plate, 65 mm x 65 mm x 10 mm, Metric | 5 | 41 | 205 | Optional but nice to store cuvettes (wide base) | https://www.thorlabs.com/item/UBP2_M
PS15M | Thorlabs | Mounting Post Spacer, Height = 15 mm | 2 | 11 | 22 | Pedestal | https://www.thorlabs.com/item/PS15M
varies | Thorlabs | 1/4-20 socket head cap screw L=37 mm | 1 | 1 | 1
RC2/M | Thorlabs | Dovetail Rail Carrier, 50.8 mm x 25.4 mm, M6 Counterbore, M4 Taps | 1 | 33 | 33 |  | https://www.thorlabs.com/item/RC2_M
Photos: docs/photos-version50mm-wide-SLSprinted(UZH)/

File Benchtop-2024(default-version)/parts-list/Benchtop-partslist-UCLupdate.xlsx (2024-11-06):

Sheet: Main
DISCLAIMER: All prices are approximate and subject to change by the vendors without prior notice
Part # | Vendor | Description | QTY | Unit Price (USD) | Price (USD) | Assembly | Subassembly | Comment
Camera
01-IRIS-15-PCIe-M-16-C | Photometrics | IRIS-15-PCIe sCMOS camera | 1 | 15000 | 15000 | Detection arm |  | FOV 25 mm diagonal, programmable rolling shutter, 15MP sensor
Excitation laser combiner options
Recommended laser combiner specs: 3-4 lasers: (405 optional), 488, 561, 638 nm, power 50-150 mW. Digital and analog power modulation. Coupling to SM fiber with FC/APC end connector.
 | Oxxius | L4Cc 488-561-638 nm, 100 mW each, 2 fiber ports, switching module MDL-FSTM | 1 | 25000 | 25000 | Excitation |  | Includes switching module between 2 laser ports, controlled by TTL signal. The 405nm is NOT included! A four-laser version is ~35k.
Sample & Microscope Stages
Dual-LS100-FTP | ASI | Two parallel LS-100 servo actuators, table mounting brackets not included | 0 | 6500 | 0 | Sample motion |  | Sample Y stage
LS-50-AMCCH | ASI | LS-50 Linear Stage, with sub-micron accuracy, and 50 mm of travel | 0 | 2250 | 0 | Sample motion |  | Sample X stage
LS-5012 | ASI | Plate for attaching flat surface of linear stage to breadboard. 3.9" x 5.9" | 0 | 160 | 0 | Detection arm | Detection path
LS-50-AMCLH | ASI | LS-50 Linear Stage, with sub-micron accuracy, and 50 mm of travel | 0 | 2250 | 0 | Detection arm | Detection path | Focus (F) stage, moves camera and detection lens assembly
DV-6010-C | ASI | Dovetail mount pair (VTS-2112 & CDZ-1010) 60 x 62 x 10 mm overall dimensions. | 0 | 230 | 0 | Sample motion |  | Cross-coupling X and Z stage adapter
LS-50S-AMECH | ASI | LS-50 Linear Stage, with sub-micron accuracy, 50 mm of travel, and stainless steel slide | 0 | 2425 | 0 | Sample motion |  | Sample Z-stage
LE-LS-HH-70 | ASI | Encoder Linear LE Heidenhain 70mm scale installed on AMECHS stage | 0 | 3000 | 0 | Sample motion |  | Sample Z-stage encoder
C60-3060-CMR-1011 | ASI | LS-50 slide to C-mount adapter | 0 | 150 | 0 | Sample motion |  | Rotary stage adapter
C60-3060-SRS | ASI | Rotary stage with collet for holding a sample. | 0 | 3000 | 0 | Sample control |  | Sample Rotation (R) stage
STAGE-4D-MESOSPIM-K1 | ASI | All stage parts above offered by ASI (Jon Daniels <jon@asiimaging.com>) | 1 | 19965 | 19965 |  |  | Bundle of 6 stages with mounting hardware
TG8-BASIC | ASI | Controller: Includes TG8, TGCOM, 2x TGDCM2, SA-JOY+ZF Contols four DC servo motors, | 0 | 5800 | 0 | Motion control |  | Motion controller with pre-installed cards
TGDCM2 | ASI | Dual Axis motion control card - one slot | 0 | 1100 | 0 | Motion control |  | Motion controller card
TG8-MESOSPIM-K1 | ASI | The controller bundle offered by ASI | 1 | 6900 | 6900 |  |  | Bundle of motion controller
MESOS-11 or mesoSPIM-Bridge-wide | ASI or Mechanical shop | Bridge part between two parallel LS-100 servo actuators | 1 | 160 | 0 | Sample motion |  | Bridge for XZR stage assembly. NOT included in the STAGE-4D-MESOSPIM-K1 (above), but included in MESOS-MACH-K1 (below).
MESOS-MACH-K1 | ASI | kit of metal machined parts for benchtop mesoSPIM | 0 | 1740 | 1740 | Sample motion and Excitation |  | Kit includes MESOS-11, qty 14 MESOS-10, and qty 2 each MESOS-01, MESOS-12, and MESOS-13
AB90H | Thorlabs | Slim Right-Angle Bracket with Counterbored Slots | 5 | 27 | 135 | Sample motion |  | 4x: Table mounting for the Y axis (two parallel LS-100 servo actuators Dual-LS100-FTP); 1x: for galvo board heat sink mounting
Sample handling
KB25/M | Thorlabs | Complete 25 mm x 25 mm Kinematic Base, Top and Bottom Plates, M4 Counterbores | 2 | 70 | 140 | Sample handling |  | Magnetic bases to attach sample holders and immersion cuvette
KBB25/M | Thorlabs | Bottom Plate Only of the KB25/M Kinematic Base, M4 Counterbore | 6 | 36 | 216 | Sample handling |  | Sample holder side (nests, not balls) of the kinematic base
TR50/M | Thorlabs | Ø12.7 mm Optical Post, SS, M4 Setscrew, M6 Tap, L = 50 mm | 1 | 6 | 6 | Sample handling |  | Connection of theta-stage chuck to the sample holder.
PH50/M | Thorlabs | Ø12.7 mm Post Holder, Spring-Loaded Hex-Locking Thumbscrew, L=50 mm | 1 | 9 | 9 | Sample handling |  | Connection of theta-stage chuck to the sample holder. Use M6 bolt in the chuck to connect
RLA150/M | Thorlabs | Dovetail Optical Rail, 150 mm, Metric | 1 | 43 | 43 | Sample handling |  | Immersion cuvette base
RC2/M | Thorlabs | Dovetail Rail Carrier, 50.8 mm x 25.4 mm, M6 Counterbore, M4 Taps | 1 | 29 | 29 | Sample handling |  | Rail carrier for immersion cuvette base
RD-PDT-S | Radiant Dyes | Prism Turn Table Small | 1 | 195 | 195 | Sample handling |  | Base for immersion cuvette
RD-PDT-S-to-M4-bolts-Base-H10mm | 3D printed | Adapter for mounting RD-PDT-S to Thorlabs rail carrier RC2, cuvettes 75 mm tall | 1 | 10 | 10 |  |  | See file RD-PDT-S-to-M4-bolts-Base-H10mm.ipt (.stl) for details.
Computer
Recommendations:128 GB RAM, 2 TB or larger SSD NVMe drive, one PCIe x1 (or higher) and one PCIe x4 (or higher) slot.
 |  | Imaging Workstation with a large screen | 1 | varies | 0
Excitation arms
PBG52522 | Thorlabs | UltraLight Series II Breadboard, 450 x 600 x 55 mm, M6 Taps | 1 | 728 | 728 | Base |  | Microscope base
AV4/M | Thorlabs | Ø45.0 mm Sorbothane Feet, Internal M6 Mounting Thread, 4 Pieces | 1 | 33 | 33 | Base |  | Attached to the bottom of the PBG52522 Breadboard. Based on Benchtop weight 25 kg on breadboard (including BB).
SM1FCA | Thorlabs | FC/APC Fiber Adapter Plate with External SM1 (1.035"-40) Threads, Wide Key (2.2 mm) | 2 | 31 | 62 | Excitation | Laser collimator | Oxxius ships with PM-S405-XP+ optical fiber, NA=0.11.
AC254-060-A-ML | Thorlabs | f=60 mm, Ø1" Achromatic Doublet, SM1-Threaded Mount, ARC: 400-700 nm | 2 | 99 | 198 | Excitation | Laser collimator | Recommended achromat, depends of optical fiber NA, see https://github.com/mesoSPIM/benchtop-hardware/wiki/Excitation-arms-assembly
SM1M20 | Thorlabs | SM1 Lens Tube Without External Threads, 2" Long, Two Retaining Rings Included | 2 | 17 | 34 | Excitation | Laser collimator | This tube is minimal , for f=50 mm achromat. It must be extended by 0.3", 0.5" or 1" tubes for f=60, 70, or 75 mm achromats.
SM1L03 | Thorlabs | SM1 Lens Tube, 0.30" Thread Depth | 2 | 12 | 24 | Excitation | Laser collimator | Tube extension for f=60 mm achromat
SM1L05 | Thorlabs | SM1 Lens Tube, 0.50" Thread Depth | 2 | 12 | 24 | Excitation | Laser collimator | Tube extension for f=70 mm achromat
SM1L10 | Thorlabs | SM1 Lens Tube, 1" Thread Depth | 2 | 14 | 28 | Excitation | Laser collimator | Tube extension for f=75 mm achromat
SM1A10 | Thorlabs | Adapter with External SM1 Threads and Internal C-Mount Threads | 2 | 18.4127496 | 36.8254992 | Excitation | Adapter
33-494 | Edmund Optics | Optotune EL-16-40-TC-VIS-5D-C lenses | 2 | 935 | 1870 | Excitation | ETL Unit
88-940 | Edmund Optics | Optotune Lens Driver EL-E-4i | 2 | 365 | 730 | Excitation | ETL Unit | Modified: BNC cables need to be soldered: see https://github.com/mesoSPIM/mesoSPIM-hardware-documentation/wiki/mesoSPIM_preparing_ETL_drivers
varies | Digitec or elsewhere | Powered USB-Hub, eg Icy Box IB-HUB1405 | 1 | 40 | 40 | Excitation | ETL Unit | Simple USB-Hub for powering the ETL-Drivers
88-941 | Edmund Optics | Optotune 6-way Hirose Male/Female Cable, 1m Length | 2 | 90 | 180 | Excitation | ETL Unit
SM1A9 | Thorlabs | Adapter with External C-Mount Threads and Internal SM1 Threads, 4.4 mm Spacer | 2 | 18 | 36 | Excitation | Adapter
SM1T2 | Thorlabs | SM1 (1.035"-40) Coupler, External Threads, 0.5" Long | 2 | 21.21 | 42.42 | Excitation | Adapter | Distance adjustment
SM1L10 | Thorlabs | SM1 Lens Tube, 1.00" Thread Depth, One Retaining Ring Included | 2 | 13 | 26 | Excitation | Adapter
KCB1E/M | Thorlabs | Right-Angle Kinematic Elliptical Mirror Mount with Tapped Cage Rod Holes, 30 mm Cage System and SM1 Compatible, M4 and M6 Mounting Holes | 4 | 189 | 756 | Excitation | Laser folding | M1, M2 fold mirrors, in each arm
BBE1-E02 | Thorlabs | 1" Broadband Dielectric Elliptical Mirror, 400 - 750 nm | 4 | 110 | 440 | Excitation | Laser folding | M1, M2 fold mirrors, in each arm
CP33/M | Thorlabs | SM1-Threaded 30 mm Cage Plate, 0.35" Thick, 2 Retaining Rings, M4 Tap | 8 | 16 | 128 | Excitation | Cage assembly | 4 per arm
AC254-100-A-ML | Thorlabs | f=100 mm, Ø1" Achromatic Doublet, SM1-Threaded Mount, ARC: 400-700 nm | 4 | 104 | 416 | Excitation | The 1:1 relay from ETL to galvo | Lenses L2, L3 in the design view
ER8-P4 | Thorlabs | Cage Assembly Rod, 8" Long, Ø6 mm, 4 Pack | 2 | 41 | 82 | Excitation | The 1:1 relay from ETL to galvo | 4 rods per arm
ER12 | Thorlabs | Cage Assembly Rod, 12" Long, Ø6 mm | 2 | 17 | 34 | Excitation | Excitation obj mount | Rods that hold the excitation objectives in 60-mm cage
ER4 | Thorlabs | Cage Assembly Rod, 4" Long, Ø6 mm | 4 | 7 | 28 | Excitation | Excitation obj mount | Rods that hold the excitation objectives in 60-mm cage
ER1 | Thorlabs | Cage Assembly Rod, 1" Long, Ø6 mm | 4 | 5 | 20 | Excitation | Excitation obj mount | Rods that hold the excitation objectives in 60-mm cage
91863 | Nikon | Nikon AF-S 50 mm f/1.4 G Objective | 2 | 400 | 800 | Excitation | Excitation obj | Modified manually
MESOS-01 or LCP31M-Nikon-modified | ASI or Mechanical workshop | Nikon objective mount using Thorlabs LCP31/M 60 mm Blank Cage Plate | 2 | 300 | 600 | Excitation | Excitation obj mount | The part is offered by ASI as "MESOS-01 - CAGE ADAPTER". If DIY, see /custom-parts/excitation-objective/LCP06M-Nikon-modified.ipt
LCP31/M | Thorlabs | 60 mm Blank Cage Plate, M4 Tap (supersedes obsolete LCP03) | 0 | 36 | 0 | Excitation | Excitation obj mount | If DIY, lathe turning or similar machining is required, see /custom-parts/excitation-objective/
SM2NFMA or (discontinued) SM2NFM | Thorlabs | Adapter with External SM2 Threads and Nikon Female F-Mount Ring | 2 | 92 | 184 | Excitation | Excitation obj mount | Goes into LCP06M-Nikon-modified. If DIY, the F-mount steel ring must be taken out and mounted into the modified LCP06M plate using screws.
Cage60mm-2sides-InnerD75mm-L75mm | 3D printed | Laser safety snap-on covers | 2 | 1 | 2 | Excitation | Excitation obj mount | See the STL file in folder /custom-parts/laser-safety/Universal-cage60mm-L75mm(Benchtop)
PH50/M | Thorlabs | Ø12.7 mm Post Holder, Spring-Loaded Hex-Locking Thumbscrew, L=50 mm | 4 | 7 | 28 | Excitation | The 1:1 relay from ETL to galvo | Optical cage support, 2 per arm
PH75/M | Thorlabs | Ø12.7 mm Post Holder, Spring-Loaded Hex-Locking Thumbscrew, L=75 mm | 2 | 8 | 16 | Excitation | Excitation obj mount
TR40/M | Thorlabs | Ø12.7 mm Optical Post, SS, M4 Setscrew, M6 Tap, L = 40 mm | 4 | 5 | 20 | Excitation | The 1:1 relay from ETL to galvo | Optical cage support, 2 per arm
TR50/M | Thorlabs | Ø12.7 mm Optical Post, SS, M4 Setscrew, M6 Tap, L = 50 mm | 2 | 5 | 10 | Excitation | Excitation obj mount
BA1S/M | Thorlabs | Mounting Base, 25 mm x 58 mm x 10 mm | 2 | 5 | 10 | Excitation | Excitation obj mount | Clamping post holders (L=75 mm, excitation objective mount) to optical table
XRN25P/M | Thorlabs | Compact 25 mm Travel Linear Translation Stage, Side Micrometer, 1/4"-20 Taps | 2 | 398 | 796 | Excitation | M3 mirror assembly | Linear stage for M2 mirror adjustment. Right-arm stage must be converted, so the adjustment screw is put on the left side of the stage. See Micrometer Conversio tab at https://www.thorlabs.com/newgrouppage9.cfm?objectgroup_id=11015
MESOS12 or mirror-bracket.ipt | ASI or Mechanical workshop | Braket for M3 kinematic mirror mount | 2 | 150 | 0 | Excitation | M3 mirror assembly | The part is offered by ASI as "MESOS-12". Bracket for M2 mirror mounting on linear stage. Folder /custom-parts/excitation-mirror-bracket/
XRN-B1/M | Thorlabs | Base Plate for Stages with 2" Dovetails, Metric Slot Spacing | 2 | 30 | 60 | Excitation | M3 mirror assembly | Adapter plate for linear stage
MESOS13 or QS15-mount-modified-Thorlabs-LCP31 | ASI or Mechanical workshop | Modified 60 mm Blank Cage Plate | 2 | 300 | 0 | Excitation | Galvo assembly | The part is offered by ASI as "MESOS-13 GALVO MOUNT" in the bundle. If DIY, see files in /custom-parts/galvo-assembly/15mm-galvo(Thorlabs-QS15)-mount/
LCP31/M | Thorlabs | 60 mm Blank Cage Plate, M4 Tap (supersedes obsolete LCP03) | 0 | 36 | 0 | Excitation | Galvo assembly | Stock material for the galvo mount. Included in ASI bundle. If DIY, needs modification (machining), see /custom-parts/galvo-assembly/15mm-galvo(Thorlabs-QS15)-mount/
LCP33B | Thorlabs | 60 mm Cage Mounting Bracket | 2 | 32 | 64 | Excitation | Galvo assembly | Bracket to attach the galvo mount to the 60 mm cage
LCP31/M | Thorlabs | 60 mm Blank Cage Plate, M4 Tap | 2 | 36 | 72 | Excitation | Galvo assembly | Side covers of the galvo assembly
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

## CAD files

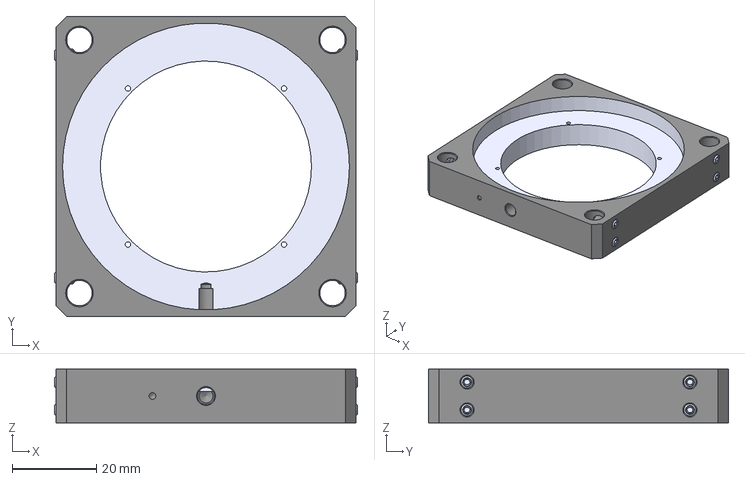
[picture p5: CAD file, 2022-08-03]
Benchtop-2024(default-version)/CAD-model-Inventor/mesoSPIM/excitation_path/components/60mm-blank-cageplate-LCP03M-Nikon-MOD.stp
71.9 x 71.1 x 12.7 mm

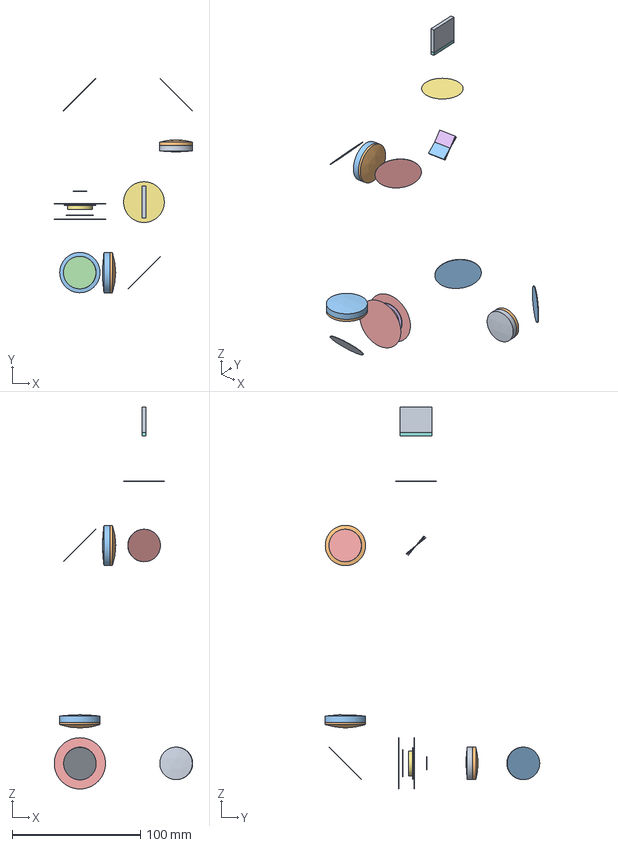
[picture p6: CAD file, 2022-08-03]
Benchtop-2024(default-version)/CAD-model-Inventor/mesoSPIM/optical_design/cad_export_v1/mesoSPIM_excitation_path_optics_V1.STP
108.0 x 167.4 x 298.1 mm

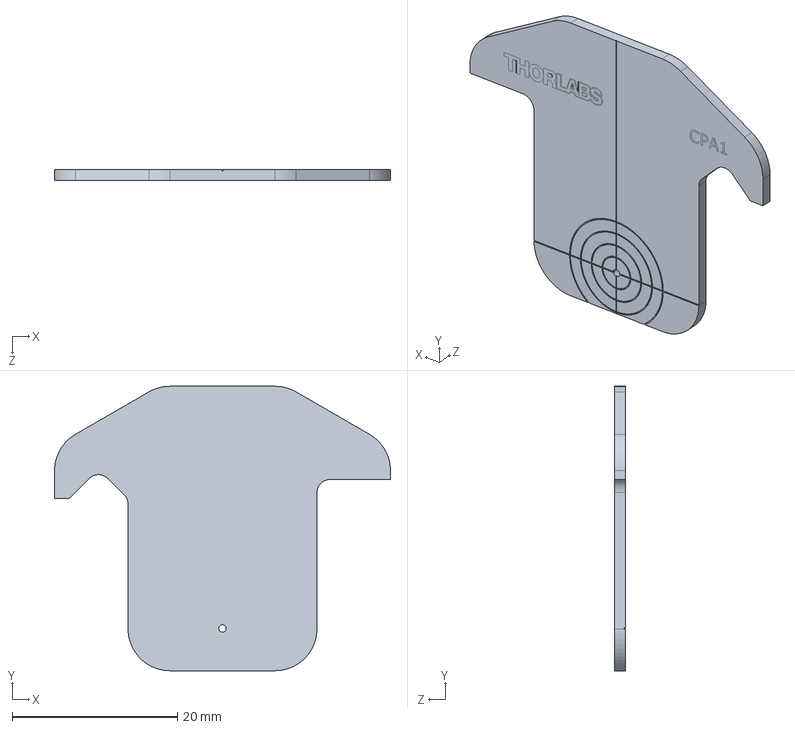
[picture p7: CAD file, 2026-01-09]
Benchtop-2024(default-version)/custom-parts/alignment_tools/CPA1.step
40.6 x 34.4 x 1.27 mm

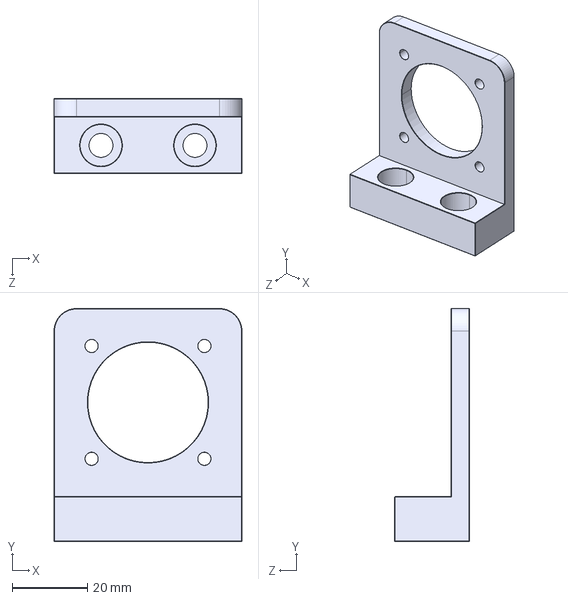
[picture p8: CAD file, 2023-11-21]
Benchtop-2024(default-version)/custom-parts/ASI-bundle/mesoS-12 - MIRROR BRACKET (CATALOG MODEL).STEP
50.0 x 62.0 x 20.0 mm

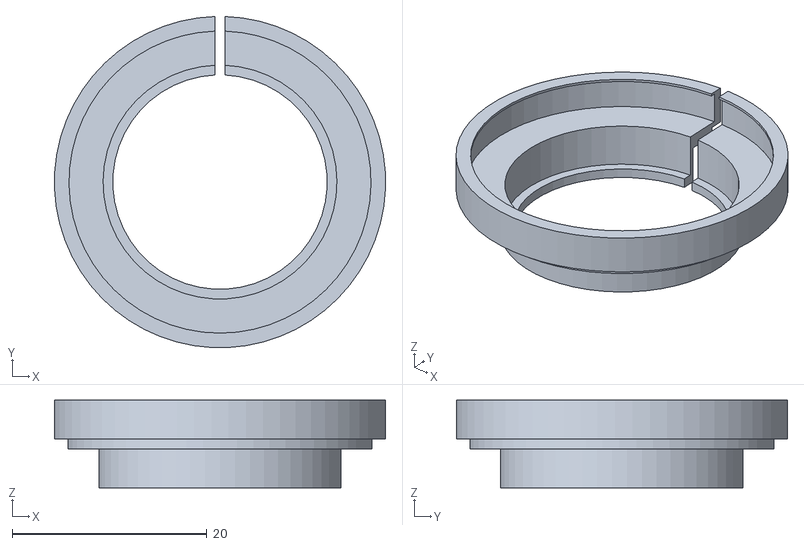
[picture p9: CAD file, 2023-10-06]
Benchtop-2024(default-version)/custom-parts/detection-accessories/FilterAdaptersVarious/FilterD32mm-SM1/32mmFilterto25mmBoreAdapter.stl
34.0 x 34.0 x 9.00

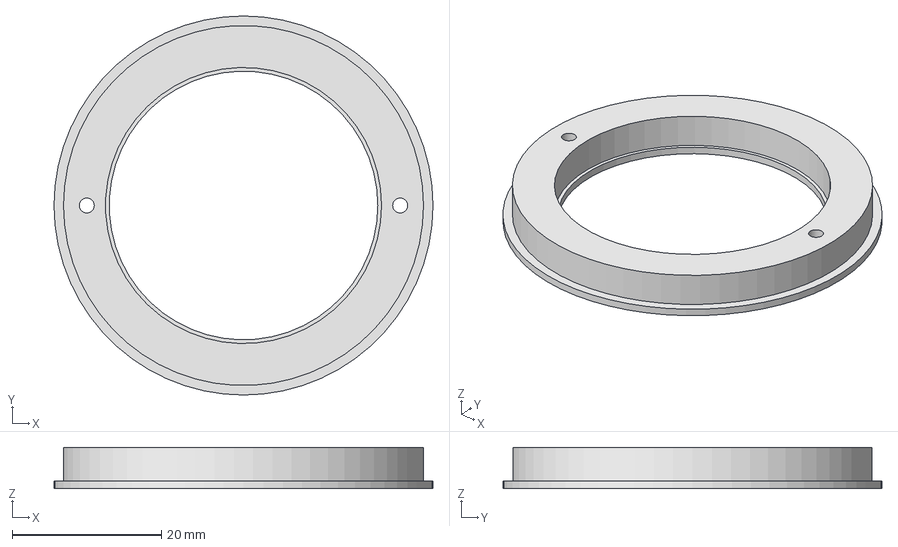
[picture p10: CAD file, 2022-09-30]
Benchtop-2024(default-version)/custom-parts/detection-accessories/FilterAdaptersVarious/FilterD37mm-SM2/Adapter-D37mm-SM2.stp
50.8 x 50.8 x 5.50 mm

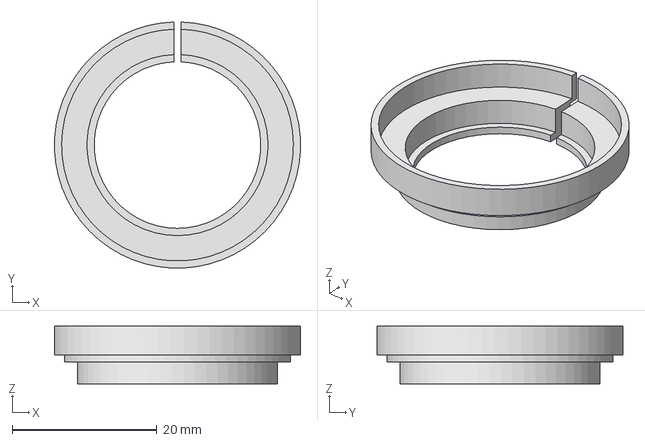
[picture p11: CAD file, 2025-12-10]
Benchtop-2024(default-version)/custom-parts/detection-accessories/FilterWheel(EFW-Mini)-Filter-Inserts/32to25mmFilterAdapter.stp
34.0 x 34.0 x 8.00 mm

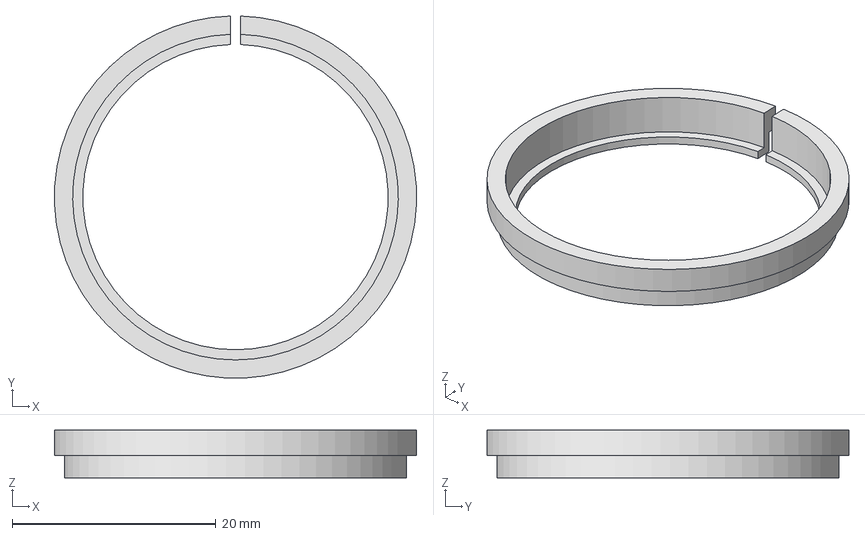
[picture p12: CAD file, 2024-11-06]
Benchtop-2024(default-version)/custom-parts/detection-accessories/FilterWheel(ZWO-7x36mm)-Filter-Inserts/32to36mm-FilterAdapter.stp
35.6 x 35.6 x 4.70 mm

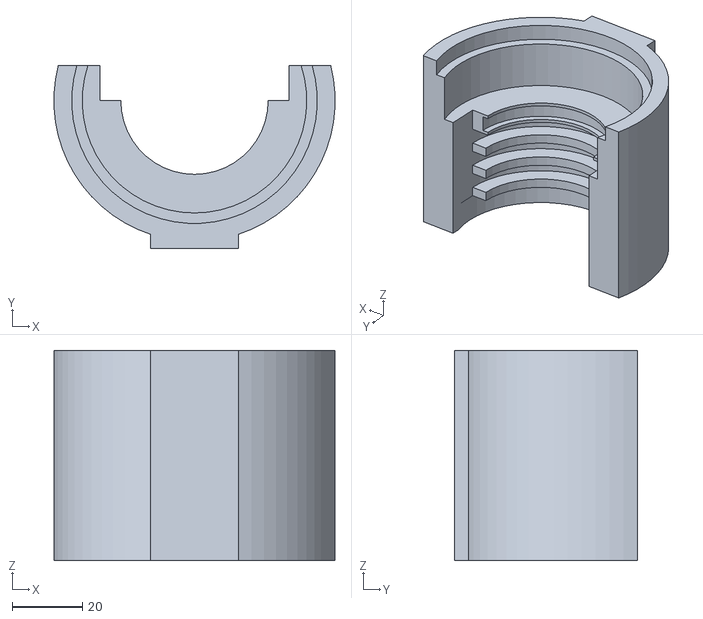
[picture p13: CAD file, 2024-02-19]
Benchtop-2024(default-version)/custom-parts/detection-accessories/HAL100-filter-holder/HAL-filter-holder1.stl
80.1 x 52.1 x 60.0

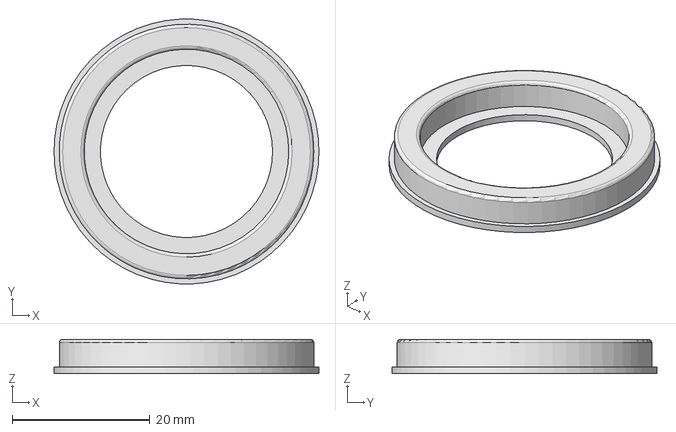
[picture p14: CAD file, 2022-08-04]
Benchtop-2024(default-version)/custom-parts/detection-accessories/Mitutoyo-BD-black-ring/Mitutoyo-BD-black-ring.stp
38.5 x 38.4 x 5.00 mm

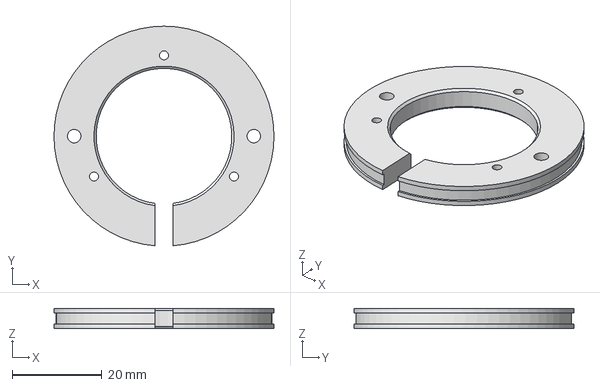
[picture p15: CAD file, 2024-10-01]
Benchtop-2024(default-version)/custom-parts/detection-accessories/Mitutoyo-MT1(tube-lens)-SM2-adapter/Adapter-MitutoyoMT1-SM2-v4(flex)-forDLP.stp
49.0 x 48.9 x 4.50 mm

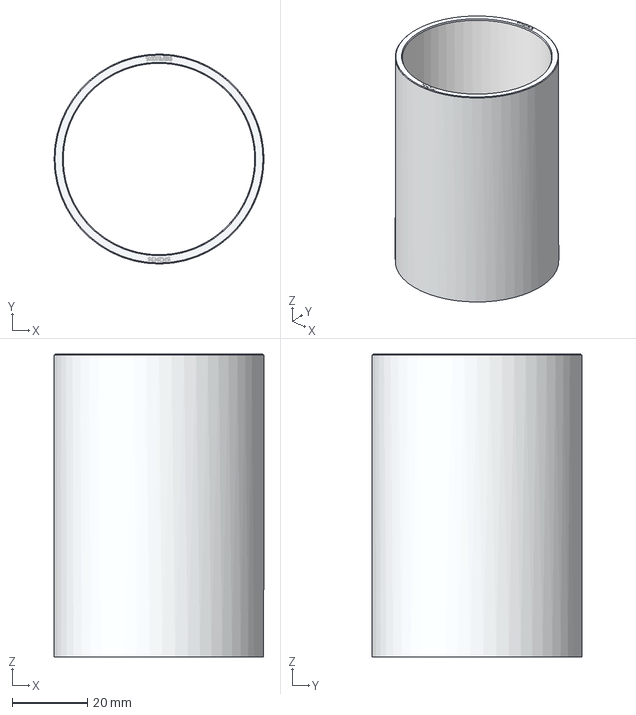
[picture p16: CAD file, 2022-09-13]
Benchtop-2024(default-version)/custom-parts/detection-accessories/Mitutoyo-Tube-Lens-Objective-assembly/SM2M35-shortened-to-80.7mm.stp
55.9 x 55.9 x 80.7 mm

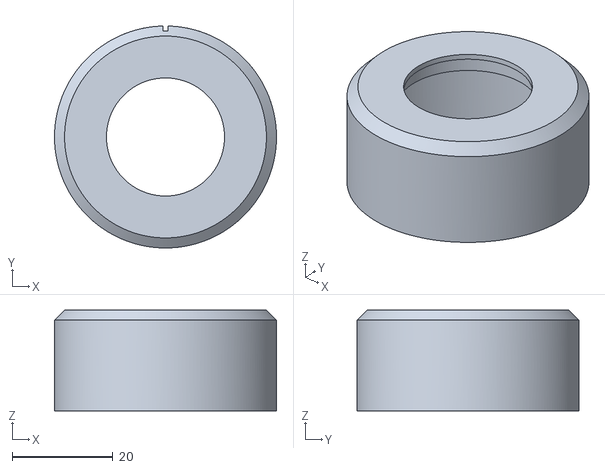
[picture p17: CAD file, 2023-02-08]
Benchtop-2024(default-version)/custom-parts/detection-accessories/PolarizerObjectiveCap-MitutoyoPlanApoBD/PolarizerObjectiveCap-MitutoyoPlanApoBD.stl
44.0 x 44.0 x 20.0

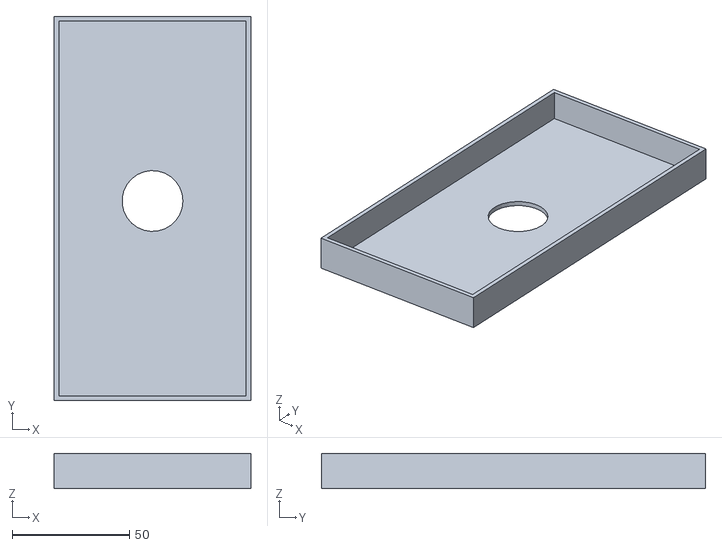
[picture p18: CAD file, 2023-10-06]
Benchtop-2024(default-version)/custom-parts/detection-accessories/SmartphoneHolder/smartphone-holder-aperture26mm.stl
84.0 x 164.0 x 15.0

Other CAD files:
Benchtop-2024(default-version)/CAD-model-Inventor/mesoSPIM/templates/mesoSPIM-Benchtop-ANSI(mm).dwg
Benchtop-2024(default-version)/custom-parts/detection-objective-mounts/Iris15-XT66P2M.stl
Benchtop-2024(default-version)/custom-parts/detection-objective-mounts/Lensagon1.2x/Lensagon1.2x-XT66P2M-BASE.stl
Benchtop-2024(default-version)/custom-parts/detection-objective-mounts/Platinum0.5x/Platinum0.5x-XT66P2M-BASE.stl
Benchtop-2024(default-version)/CAD-model-Inventor/mesoSPIM/detection_path/Mitutoyo/Mitutoyo-BD-Plan-Apo-system.iam
Benchtop-2024(default-version)/CAD-model-Inventor/mesoSPIM/detection_path/Mitutoyo/TubeLensWAdapter.iam
Benchtop-2024(default-version)/CAD-model-Inventor/mesoSPIM/detection_path/components/Lensagon1.2x-XT66P2M(ThorlabsRailCarriage).ipt
Benchtop-2024(default-version)/CAD-model-Inventor/mesoSPIM/detection_path/components/Servo-Dynamixel-Adapter-V2.ipt
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

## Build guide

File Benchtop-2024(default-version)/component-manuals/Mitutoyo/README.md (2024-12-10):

# Dataseheets and CAD models for Mitutoyo objectives
More information: https://sensing.mitutoyo.co.jp/en/

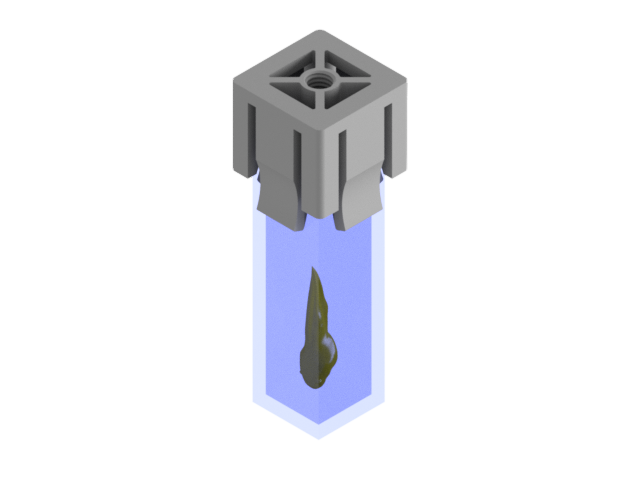
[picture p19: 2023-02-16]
Benchtop-2024(default-version)/custom-parts/sample_handling/assemblies/UQ204-topHolder-sample(tadpole-blueTint).png

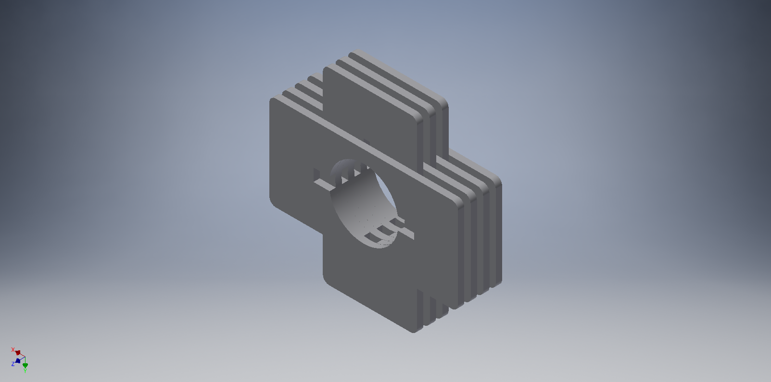
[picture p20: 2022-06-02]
Benchtop-2024(default-version)/custom-parts/galvo-assembly/15mm-galvo(Thorlabs-QS15)-mount/HeatSink-sheet-assembly-H14mm.bmp

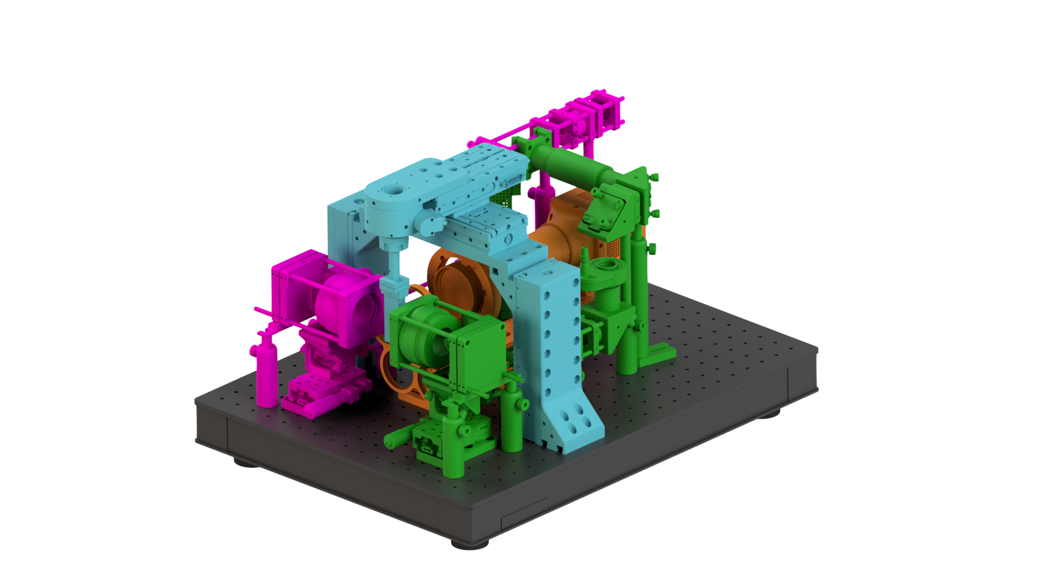
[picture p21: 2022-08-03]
Benchtop-2024(default-version)/CAD-model-Inventor/mesoSPIM/renderings/overview/view3/benchtop-mesoSPIM-V2-1-step5.png

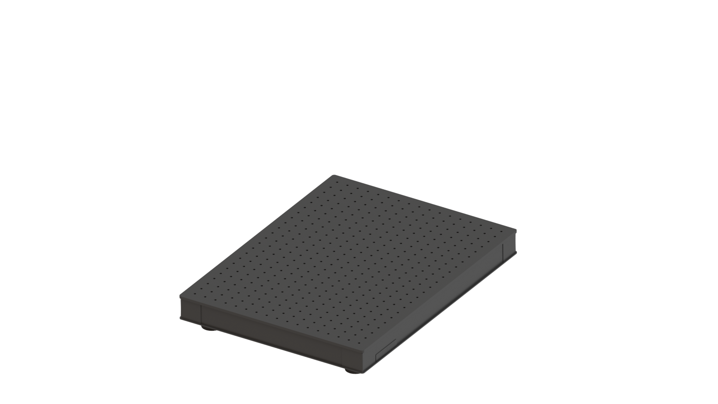
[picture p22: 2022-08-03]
Benchtop-2024(default-version)/CAD-model-Inventor/mesoSPIM/renderings/overview/view1/benchtop-mesoSPIM-V2-step1.png

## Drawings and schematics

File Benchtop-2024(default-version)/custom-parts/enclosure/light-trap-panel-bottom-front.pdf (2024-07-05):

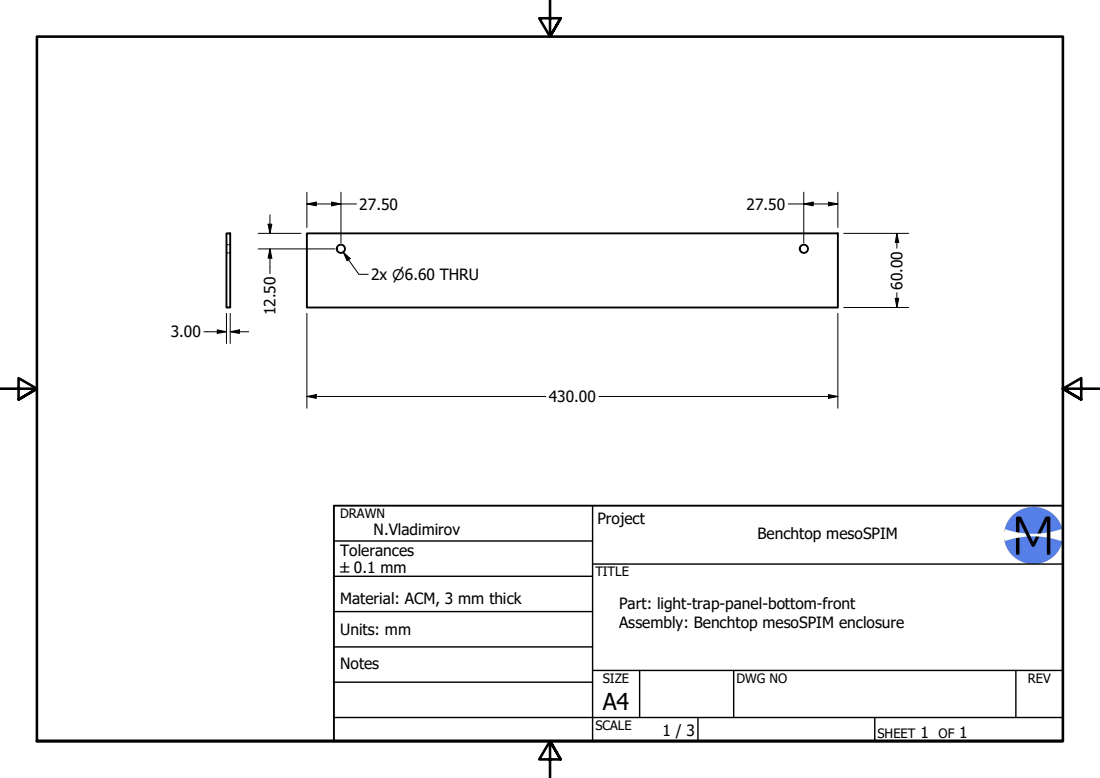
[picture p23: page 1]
Benchtop mesoSPIM; Units: mm; 2x ⌀6.60 THRU

Material: ACM, 3 mm thick

Part: light-trap-panel-bottom-front
Assembly: Benchtop mesoSPIM enclosure

SIZE A4 | | DWG NO | REV

SCALE 1 / 3 | | SHEET 1 OF 1

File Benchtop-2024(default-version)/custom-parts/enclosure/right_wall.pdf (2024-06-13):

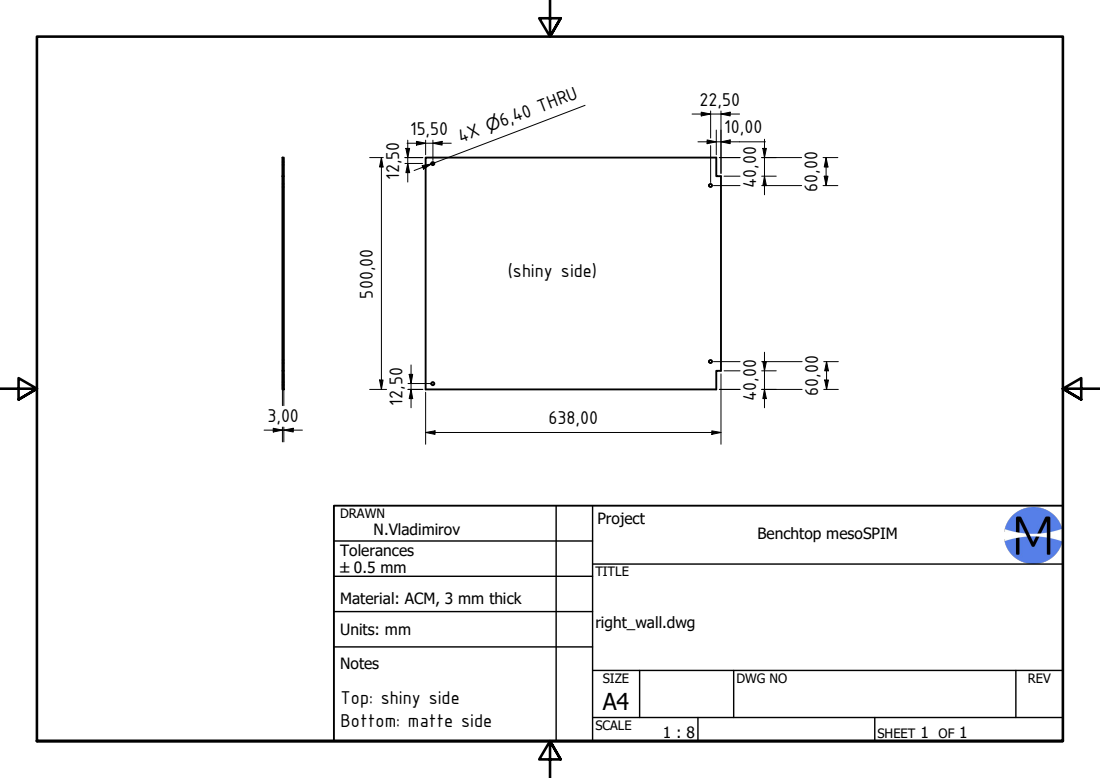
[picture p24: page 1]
(shiny side); 4X ⌀6,40 THRU

DRAWN N.Vladimirov | Project Benchtop mesoSPIM

Tolerances `0.5 mm

Material: ACM, 3 mm thick

Units: mm

Notes Top: shiny side Bottom: matte side

SIZE A4 | DWG NO | REV

SCALE 1 : 8 | SHEET 1 OF 1

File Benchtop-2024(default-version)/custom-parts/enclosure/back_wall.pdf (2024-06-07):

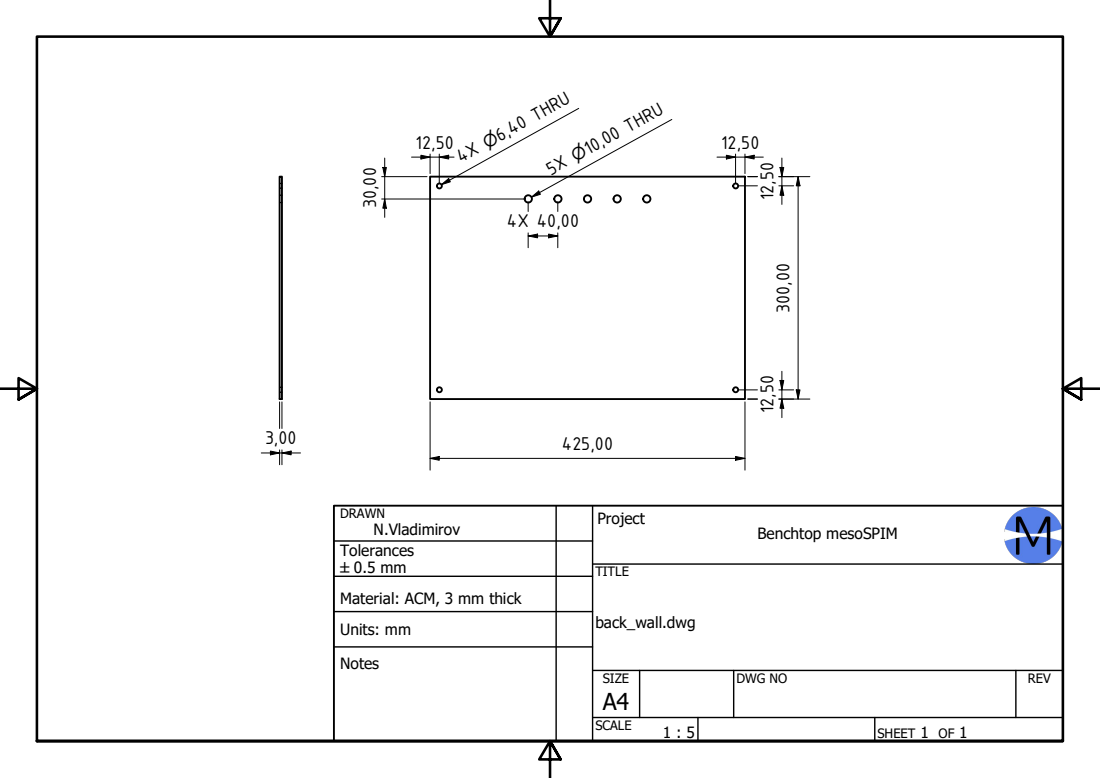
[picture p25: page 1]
4X ⌀6,40 THRU 5X ⌀10,00 THRU

DRAWN N.Vladimirov | Project Benchtop mesoSPIM

Tolerances `0.5 mm

Material: ACM, 3 mm thick

Units: mm

Notes

SIZE A4 | DWG NO | REV

SCALE 1 : 5 | SHEET 1 OF 1

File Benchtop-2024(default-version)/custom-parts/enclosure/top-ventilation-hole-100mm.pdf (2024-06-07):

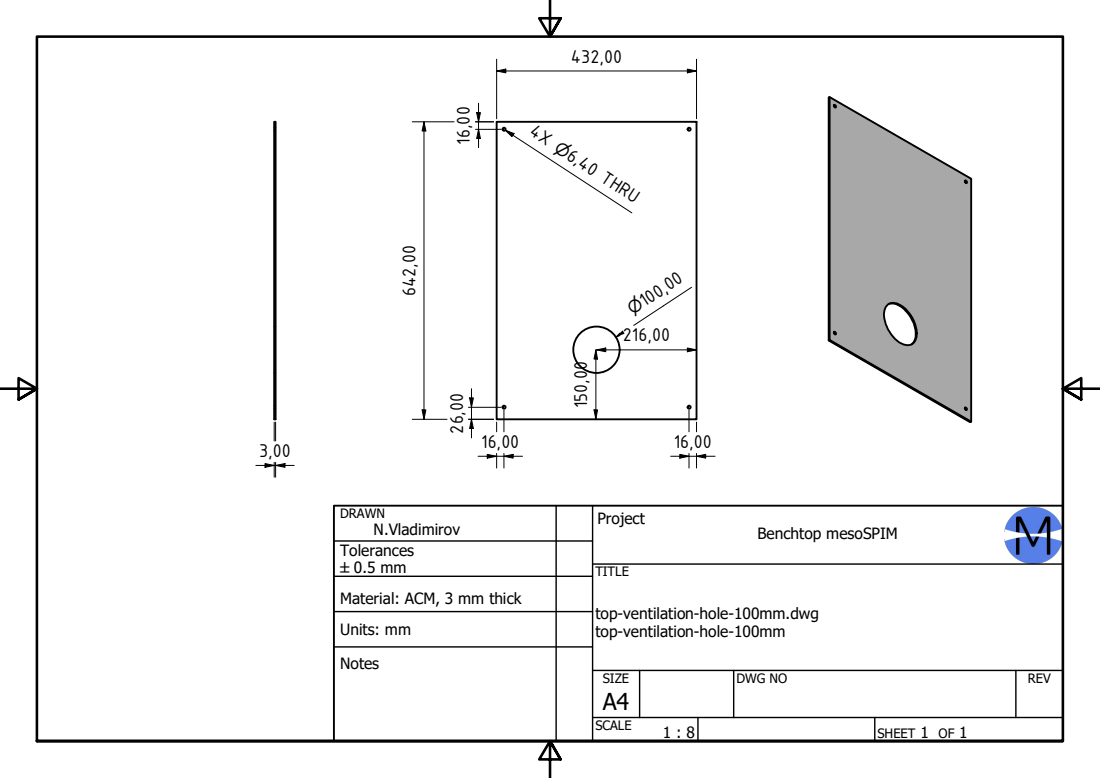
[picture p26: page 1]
4X ⌀6,40 THRU

DRAWN N.Vladimirov | Project Benchtop mesoSPIM

Tolerances `0.5 mm

Material: ACM, 3 mm thick

top-ventilation-hole-100mm.dwg
top-ventilation-hole-100mm

Units: mm

Notes

SIZE A4 | DWG NO | REV

SCALE 1 : 8 | SHEET 1 OF 1

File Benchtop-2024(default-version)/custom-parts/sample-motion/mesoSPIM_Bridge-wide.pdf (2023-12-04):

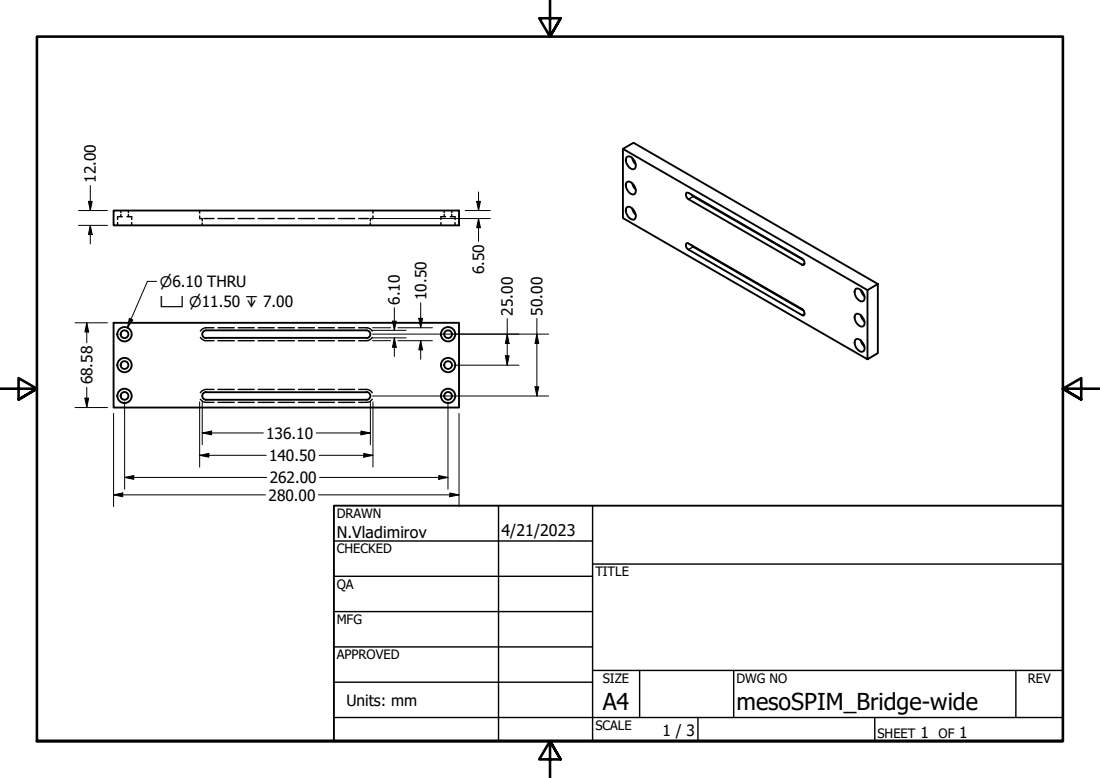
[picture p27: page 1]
⌀6.10 THRU

DRAWN N.Vladimirov | 4/21/2023

CHECKED

MFG

APPROVED

SIZE A4 | DWG NO mesoSPIM_Bridge-wide | REV

Units: mm

SCALE 1 / 3 | SHEET 1 OF 1

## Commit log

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2022-02-07 preliminary BOM, lens overview
    [Benchtop-partslist-latest.xlsx, Telecentric_Lens_Overview.xlsx]
2022-02-10 parts and lens testing added, lens mag 1.2
    [Benchtop-partslist-latest.xlsx, Galvo-bracket-modified.ipt, Galvo-bracket-original.ipt, LCP03M_modified.ipt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]
2022-02-11 Olympus MVPLAPO 1x contrast maps for various zooms
    [Lensagon1.2x-ThorlabsRailCarriage(XT66P2M).0010.ipt, Lensagon1.2x-ThorlabsRailCarriage(XT66P2M).ipt]
2022-02-14 lens mount for Lensagon 1.2x
    [Lensagon1.2x-ThorlabsRailCarriage(XT66P2M).0010.ipt, Lensagon1.2x-ThorlabsRailCarriage(XT66P2M).0014.ipt, Lensagon1.2x-ThorlabsRailCarriage(XT66P2M).ipt, Lensa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]
2022-02-28 3D printed parts and BOM update
    [Benchtop-partslist-latest.xlsx, Lensagon1.2x-XT66P2M.ipt, RD-PDT-S-to-RC2-height10mm.ipt, RD-PDT-S-to-RC2-height20mm.ipt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]
2022-03-01 update detection filter wheel with motorized flip mount
    [Benchtop-partslist-latest.xlsx]
2022-04-07 laser safety snap-on covers; filter wheel servo supplier change to Mouser
    [Benchtop-partslist-latest.xlsx, Cage30mm-2sides-L100mm.ipt, Cage30mm-2sides-L100mm.stl, Cage30mm-2sides-L100mm.stp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]
2022-04-16 remove version from folder name
    [Benchtop-partslist-latest.xlsx, Cage30mm-2sides-L100mm.ipt, Cage30mm-2sides-L100mm.stl, Cage30mm-2sides-L100mm.stp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]
2022-04-26 add CAD models: det-objective holders, filter wheel
    [Benchtop-partslist-latest.xlsx, FilterWheel-2inch-5pos.ipt, FilterWheel-2inch-5pos.stl, Lensagon1.2x-XT66P2M-BASE.0001.ipt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]
2022-05-03 excitation cage table mount H25 mm model for 3D print
    [Telecentric_Lens_Overview.xlsx, cage2table-mount-M4(top)-M6(bottom).ipt]
2022-05-18 update BOM with 15 mm galvos and accessories
    [Benchtop-partslist-latest.xlsx]
2022-06-02 create galvo mount for 15-mm galvos Thorlabs QS15
    [06-631-110_B01 (Iris 15 PCIe) Shell.iam, 10-608-007_91290A102.ipt, 10-631-108_91290A019.ipt, 10-631-109_91290A013.ipt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]
2022-06-02 Thorlabs QS-15 galvo mounting plate, modified LCP03 drawing
    [QS15-mount-modified-Thorlabs-CagePlate-LCP03.0013.ipt, QS15-mount-modified-Thorlabs-CagePlate-LCP03.0014.ipt, QS15-mount-modified-Thorlabs-CagePlate-LCP03.0015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]
2022-06-02 cage to table clamps 3D printable
    [cage2table-mount-M4(top)-M6(bottom)-H50mm.ipt, cage2table-mount-M4(top)-M6(bottom)-H50mm.stl, cage2table-mount-M4(top)-M6(bottom).0001.ipt]
2022-06-02 QS15 galvo assembly
    [15mm-QS15-galvo-assembly.0002.iam, 15mm-QS15-galvo-assembly.iam, CagePlate-LCP03_M.ipt, CagePlate-LCP03_M.step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]
2022-06-02 heat sink model, lathe required
    [15mm-QS15-galvo-assembly.0002.iam, 15mm-QS15-galvo-assembly.0006.iam, 15mm-QS15-galvo-assembly.iam, Galvo-QS15X.0005.ipt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]
2022-06-02 QS15 galvo heat sink drawing, PDF
    [HeatSink-H14p6mm.0001.ipt, HeatSink-H14p6mm.0002.dwg, HeatSink-H14p6mm.0002.ipt, HeatSink-H14p6mm.dwg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]
2022-06-02 cage support redesign, stiffer legs
    [cage2table-mount-M4(top)-M6(bottom)-H50mm.0003.ipt, cage2table-mount-M4(top)-M6(bottom)-H50mm.ipt, cage2table-mount-M4(top)-M6(bottom)-H50mm.stl, cage2table-mo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]
2022-06-02 galvo heatsink design from sheet metal
    [15mm-QS15-galvo-assembly.0006.iam, 15mm-QS15-galvo-assembly.0009.iam, 15mm-QS15-galvo-assembly.iam, HeatSink-H14p6mm.dwg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]
2022-06-15 Oxxius cabling SMB
    [Benchtop-partslist-latest.xlsx]
2022-06-16 excitation objective cage support, BOM update
    [Benchtop-partslist-latest.xlsx, cage2table-mount-M4(top)-M6(bottom)-H100mm-W35mm.stl, cage2table-mount-M4(top)-M6(bottom)-H100mm.0001.ipt, cage2table-mount-M4(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]
2022-06-21 3D model legs w 5 mm offset; objectives list update
    [Benchtop-partslist-latest.xlsx, Telecentric_Lens_Overview.xlsx, cage2table-mount-M4(top)-M6(bottom)-H100mm-HoleOffset5mm.0009.ipt, cage2table-mount-M4(top)-M6(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]
2022-07-06 objectives update
    [Detection-obj-overview.xlsx, Telecentric_Lens_Overview.xlsx]
2022-07-13 galvo mount and heat sink renderings
    [15mm-QS15-galvo-assembly.0009.iam, 15mm-QS15-galvo-assembly.0011.iam, 15mm-QS15-galvo-assembly.iam, HeatSink-sheet-assembly-H14mm.0001.iam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]
2022-07-13 Nikon CFI Plan Fluor added
    [Detection-obj-overview.xlsx]
2022-07-14 update Thorlabs adapers
    [Detection-obj-overview.xlsx]
2022-08-03 add excitation mirror bracket 3D printable; clean up parts list.
    [Benchtop-partslist-latest.xlsx, mirror-bracket.0003.ipt, mirror-bracket.ipt, mirror-bracket.stl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]
2022-08-03 filter wheel upd
    [FilterWheel-Dynamixel(MX28).iam]
2022-08-03 add full CAD model, Inventor 2021, for version control and backup
    [0_95x_iris_macro_detection_path.0002.iam, 0_95x_iris_macro_detection_path.iam, 10x20-plunger-V1.0001.ipt, 10x20-plunger-V1.ipt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]
2022-08-03 some parts Inventor version downgrade for compatibility
    [06-631-110_B01 (Iris 15 PCIe) Shell.iam, 10-608-007_91290A102.ipt, 10-631-108_91290A019.ipt, 10-631-109_91290A013.ipt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]
2022-08-04 black ring light trap for Mitutoyo BD objectives
    [Mitutoyo-BD-black-ring.ipt, Mitutoyo-BD-black-ring.stl, Mitutoyo-BD-black-ring.stp]
2022-08-04 Mitutoyo Plan Apso are amazing
    [Detection-obj-overview.xlsx]
2022-08-10 laser cover model update
    [Benchtop-partslist-latest.xlsx, Cage60mm-2sides-InnerD75mm-L100mm.ipt, Cage60mm-2sides-InnerD75mm-L100mm.stl, Cage60mm-2sides-InnerD75mm-L100mm.stp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]
2022-08-19 galvo fans with 60 mm cage mounts
    [Benchtop-partslist-latest.xlsx, Fan-mount-modified-Thorlabs-CagePlate-LCP03.0020.ipt, Fan-mount-modified-Thorlabs-CagePlate-LCP03.ipt, Fan-mount-modified-Thorl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]
2022-08-19 add Mitutoyo detection objectives
    [Benchtop-partslist-latest.xlsx]
2022-08-19 create ASI bridge wide, for galvo fan accommodation
    [15mm-QS15-galvo-assembly.0015.iam, 15mm-QS15-galvo-assembly.iam, HeatSink-H14p6mm.0002.dwg, HeatSink-H14p6mm.0002.ipt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]
2022-08-26 update about Leica 1x
    [Detection-obj-overview.xlsx]
2022-08-31 galvo fan mount update
    [Benchtop-partslist-latest.xlsx, Clamp-UG205(204)_100881(1mm Gelenke 2Stk.)_B.step, Clamp-UG205(204)_100881(Quadratisch Gelenke 2 Stk.)_B.step, agarose-mold-mou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]
2022-09-01 detection parts update
    [Benchtop-partslist-latest.xlsx]
2022-09-05 upload latest compliant cuvette holders
    [Clamp-UG205(204)_100881(1mm Gelenke 2Stk.)_B.0001.ipt, Clamp-UG205(204)_100881(1mm Gelenke 2Stk.)_B.ipt, Clamp-UG205(204)_100881(1mm Gelenke 2Stk.)_B.stl, Clam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]
2022-09-06 Fan-50mm mount model
    [Fan40mm-mount-modified-Thorlabs-CagePlate-LCP03.ipt, Fan40mm-mount-modified-Thorlabs-CagePlate-LCP03.stl, Fan40mm-mount-modified-Thorlabs-CagePlate-LCP03.stp, 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]
2022-09-08 Mitutoyo Plan Apo BD CAD model
    [Detection-obj-overview.xlsx, Mitutoyo-BD-Plan-Apo-system.iam]
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2022-09-13 major model update
    [15mm-QS15-galvo-assembly.0015.iam, 15mm-QS15-galvo-assembly.0016.iam, 15mm-QS15-galvo-assembly.iam, Clamp-assembly.0003.iam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]
2022-09-13 excitation mirror model: wider aperture
    [mirror-bracket.0003.ipt, mirror-bracket.0004.ipt, mirror-bracket.ipt, mirror-bracket.stl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]
2022-09-13 clamp view 1
    [ThorlabsSM2L30-XT66P2M.0015.ipt, ThorlabsSM2L30-XT66P2M.0016.ipt, ThorlabsSM2L30-XT66P2M.ipt]
2022-09-30 detection path adapters
    [Adapter-D37mm-SM2.0002.ipt, Adapter-D37mm-SM2.ipt, Adapter-D37mm-SM2.stl, Adapter-D37mm-SM2.stp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]
2022-10-03 update tube lens MT-1
    [Benchtop-partslist-latest.xlsx]
2022-10-14 clean up BOM
    [Benchtop-partslist-latest.xlsx]
2022-10-19 Tube lens update, laser cover 1-sided (chamber side)
    [Cage60mm-1side-InnerD75mm-L100mm.0002.ipt, Cage60mm-1side-InnerD75mm-L100mm.ipt, Cage60mm-1side-InnerD75mm-L100mm.stl, Cage60mm-1side-InnerD75mm-L100mm.stp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]
2022-11-11 filter wheel models, highly optional
    [FilterWheel-2inch-5pos.ipt, FilterWheel-2inch-5pos.stl, FilterWheel-Dynamixel(MX28).iam, FilterWheel-M40-5pos.0002.ipt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]
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2023-01-11 create mount for 0.9x telecentric lens. Give warning for 0.5x lens due to galvo issues.
    [Detection-obj-overview.xlsx, Platinum0.9x-XT66P2M.0019.ipt, Platinum0.9x-XT66P2M.ipt, Platinum0.9x-XT66P2M_BASE.ipt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]
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2024-02-13 fix: 3D printing instructions for laser cover.
    [Benchtop-partslist-latest.xlsx]
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2024-05-14 fixed Thorlabs BNC cable part number and PCIe-8363 card number
    [Benchtop-partslist-latest.xlsx]
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2024-06-13 fix: missing dimensions, enclosure
    [right_wall.dwg]
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2024-08-27 fix model error
    [2x-servo-boards-QS-series.dwg, 2x-servo-boards-QS-series.ipt]
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2024-10-02 fix seat depth
    [Iris15-XT66P2M_H94mm(axis2base).ipt, Iris15-XT66P2M_H94mm(axis2base).stl, Iris15-XT66P2M_H94mm(axis2base).stp]
2024-10-18 models correction
    [25to36mm-FilterAdapter.ipt, 25to36mm-FilterAdapter.stl, 25to36mm-FilterAdapter.stp, 32to36mm-FilterAdapter.ipt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]
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2025-09-05 fix file names
    [cuvette-v1.SLDPRT, cuvette-v1.STEP, cuvette-v1.STL, parts-list-immersion-cuvette.xlsx]
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2025-10-30 fix dimensions error
    [cuvette-w70mm-slide50x75mm-v1.ipt, cuvette-w70mm-slide50x75mm-v1.stl, cuvette-w70mm-slide50x75mm-v1.stp]
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2025-12-10 corrected slot depth
    [cuvette-w70mm-slide50x75mm-v2.stl, cuvette-w70mm-slide50x75mm-v2.stp]
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
